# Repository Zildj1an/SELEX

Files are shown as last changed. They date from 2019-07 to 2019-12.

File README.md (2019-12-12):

# SELEX Process with Artificial Intelligence 👨‍🔧

 




## [0] Introduction 📄

This was a long project that involved:

 * [1] The robotic automatization of biotechnological protocols.
 
      All the custom hardware design can be found at OT_Robot/harware_design.
 * [2] The usage of Artifical Intelligence.
 * [3] A search engine.
 * [4] A tool to migrate WordPress websites to the iGem servers.
 * [5] And many, many custom hardware.

You can find information on installation and usage at the end [5] and our <a href = "https://2019.igem.org/Team:MADRID_UCM/Hardware">website</a>.

## [1] Biotechnological Designs 🔬

Folder OT_Robot contains biotechnological protocols for obtaining trained libraries of DNA aptamer molecules automated with the Opentrons OT-2 robot. This protocol is part of our contribution to the 2019 iGEM international biotechnology competition. For the thermocycler we built the Ninja-PCR(original from [hisashin](https://github.com/hisashin/NinjaPCR/)). More information about the entire project can be found in our <a href = "https://2019.igem.org/Team:MADRID_UCM/Landing">website</a>.

Aptamers are a cutting-edge technology that is revolutionizing biotechnology, from biosensing to synthetic biology. Aptamers are single-strand DNA molecules that hold nature’s most important information: our genetic code. But instead of using DNA for carrying information, our aptamers depend on DNA’s 3-dimensional shape. 

We genetically engineer this shape to take hold of and mesh with our target molecule. DNA’s unique role in nature gives aptamers amazing characteristics, making them robust, stable, and cheap to produce. 

The small-sized thermal cycler is controlled via motherboard Ninja-PCR Arduino-alike, as shown above, manually welded, whose code is in NinjaPCR [folder](https://github.com/Zildj1an/SELEX/tree/master/NinjaPCR). You can update a new binary since ESP8266 SystemOnChip includes the TCP/IP stack. We also recommend the usage of an external Raspberry Pi to uninterruptedly provide the robot with Wi-Fi. You can find more information about usage at [5].

 

## [2] Artificial Intelligence Algorithm: GAN network 🤖

We also did an **Artificial Intelligence algorithm** to predict the optimal DNA molecule shapes. It is a Generative adversarial network, divided in two neuronal networks: the Generative and the Discriminative. CNN nets are used. 



## [3] iGem Search Engine 🔍 

In addition, you can use our Search Engine for words in previous or this year's team's websites. This is a python search engine with GUI for searching words in each competition year and team's website.

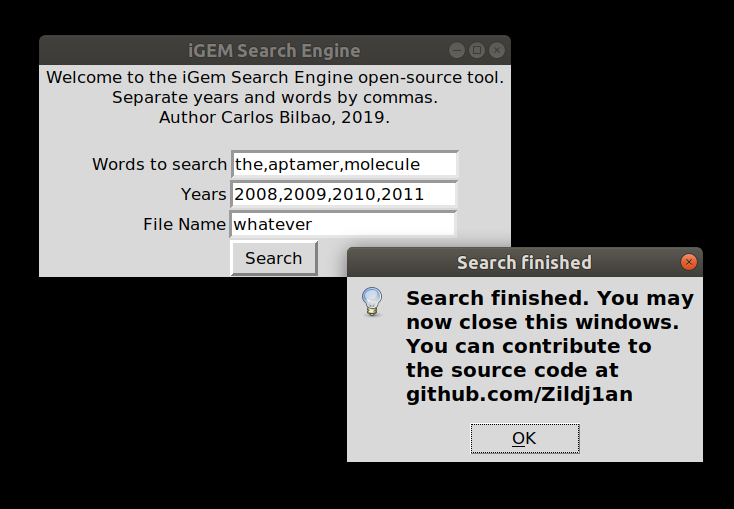
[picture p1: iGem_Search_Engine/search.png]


# [4] A tool to migrate WordPress websites to the iGem servers.

We also developed a tool to make life easier to web page developers at the iGem competition. You can use WordPress templates to develop your site and then migrate it easily with this multi-threaded script located at Tool_Migrate folder.

To run the script you can do:

```
$ bash treatment.sh [url_1] -nm - - [url_2]
```

Some additional options are available, feel free to navigate throw our code!

# [5] Hardware Design 🔋 

## Potentiostat

To assemble the potentiostat, first you should send to manufacture the PCB, in our instance we sent it to JLPCB (https://jlcpcb.com/) and buy the components listed on the Bill of Materials file. After that, you should solder those materials on the PCB. You can also request them to solder the components, if they have them.

Any team could reproduce this potentiostat sending the gerber and the NC Drill files to the manufacturer.

Regarding to the case, we designed it with a 3D modelling software, and we cut the flat faces in methacrylate with a laser cutter machine and otherwise we printed it with a 3D printer.

The PCB was made with the Altium Designer software. Altium can export PCB and schematic files as ACCEL-ASCII files. With these files you can import them to Eagle.



## Fluorimeter
To assemble the fluorimeter, you should send to manufacture the PCB, for instance we sent it to JLPCB (https://jlcpcb.com/) and buy the components listed on the Bill of Materials file. After that, you should solder those materials on the PCB. You can also request them to solder the components, if they have them.

Any team could reproduce this fluorimeter sending the gerber and the NC Drill files to the manufacturer. The PCB was made with the Altium Designer software. Altium can export PCB and schematic files as ACCEL-ASCII files. With these files you can import them to Eagle.

In relation to the case, we designed it with a 3D modelling software, and we cut the faces in methacrylate with a laser cutter machine.

## Wax Module
Wax Module
To assemble the Wax Module, you should send to manufacture the PCB, in our instance we sent it to JLPCB (https://jlcpcb.com/) and buy the components listed on the Bill of Materials file. After that, you should solder those materials on the PCB. You can also request them to solder the components, if they have them.

Any team could reproduce this module sending the gerber and the NC Drill files to the manufacturer.

The PCB was made with the Eagle software. To generate the necessary files, you can follow the JLPCB guide (https://support.jlcpcb.com/article/43-how-to-export-eagle-pcb-to-gerber-files).

In relation to the case, we designed it with a 3D modelling software, and we cut the faces with a laser cutter and the part where the resistances are located, was printed with an aluminium printer. Also, the part where the stamps are placed can be printed with a 3D printer.

## PCR, Thermal Modules
To assemble the NinjaPCR, you can make it yourself following the instructions written on their webpage or buy it (https://ninjapcr.tori.st/en/index.html).

To assemble the Thermal Module, you can send to manufacture the PCB, in our instance we sent it to JLPCB (https://jlcpcb.com/) and buy the components listed on the Bill of Materials file. After that, you should solder those materials on the PCB. You can also request them to solder the components, if they have them. The other option you could buy it from their webpage.

In relation to the case, we redesigned the NinjaPCR case with a 3D modelling software, and we cut the faces with a laser cutter in methacrylate and in wood. 

We redesigned it because we used another fan.



## Shaker Module
To assemble the Shaker Module, you should send to manufacture the PCB, in our instance we sent it to JLPCB (https://jlcpcb.com/) and buy the components listed on the Bill of Materials file. After that, you should solder those materials on the PCB. You can also request them to solder the components, if they have them.

Any team could reproduce this module sending the gerber and the NC Drill files to the manufacturer.

The PCB was made with the Eagle software. To generate the necessary files, you can follow the JLPCB guide (https://support.jlcpcb.com/article/43-how-to-export-eagle-pcb-to-gerber-files).

In relation to the case, we designed it with a 3D modelling software, and we printed the module with a 3D printer.

We also designed some PCBs from ourselves to make things easier and make them fit in the robot. We used a 3D-printer for some of our designs to store Eppendorf and Falcon tipracks. We also deisgned a PCB for a potenciostat microcontroller Teensy 3.0 and an auxiliar thermic module to cool to 4 degrees Celsius, and so on.

The 3D-designs will are available at the folder OT_Robot/hardware_design

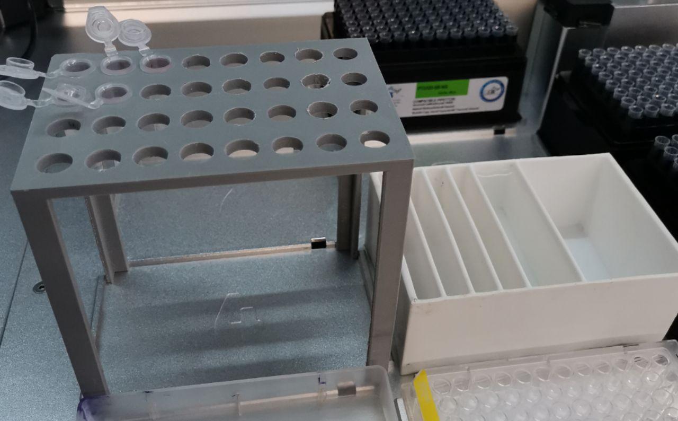
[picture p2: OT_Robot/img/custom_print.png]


## [6] Installation and Usage ❓

Our project has a lot of software involved, including:

1. A graphical Search Engine for words in websites of previous years of iGem:
   
You can run it from your terminal using:
```
$ python search.py
```
You might have some dependencies not installed, you just need to do:
```
$ sudo pip install <dependencies>	
```

2. The Aptamer Folding:

In the folder DB_Creation, execute (if you use Mac or Linux), for terminal:
```
$ python DB_Creation_Terminal.py
```
You can also speed things up with threads with bash run_several.sh, but be aware that you would need to modify the absolute path to the Rosetta software.

In the folder GAN_Network, from terminal:
```
$ python Main.py
```
Other files that could be used:

3D_structure_creation_in_pdb.py Creates only one PDB for the DDBB (testing puposes)

GAN_Network.py (Same thing as GAN_Network folder but in one file)

3. OT_Robot protocols

It contains tons of biotechnological protocols automated for the Opentrons OT2 robot in Python. The most important one is the SELEX process. To run these protocols you just need to drug and drop the protocols into the OT2 app.

You can also find in here the hardware design.

You can clone this repo or download the zip. Make sure all the dependencies are covered. First line is for installation of pip at most Linux distributions.

```
$ sudo apt install python-pip || pacman -S python-pip
$ sudo pip install opentrons subprocess time os
```
The robot uses the audio robot.mp3 and gets it from Robot Raspberry's /mnt/usbdrive/ (put it there or edit the location).
You can load the protocol in the Opentrons application, available <a href = "https://opentrons.com/ot-app">here</a>.
We also recommend the usage of an external Raspberry Pi to uninterruptedly provide the robot with Wi-Fi. Once you have stablished the Wi-Fi network at the Raspberry, you can connect the Robot too:

```
# nmcli dev wifi connect <userSSID> password <passwdSSID>
```
After the last update of the Robot -by the time this is written- the SSH connection has changed and now you need to exchange with it a public key for a more secure connection. Then when connected the robot will request the passphrase, at least the first time. Here is how you create the public key (you probably already have one):

```
$ ssh-keygen
Generating public/private rsa key pair.
Enter file in which to save the key (/home/.ssh/id_rsa):
/home/pepe/.ssh/id_rsa already exists.
Overwrite (y/n)?
Enter passphrase (empty for no passphrase):
Your identification has been saved in /home/.ssh/id_rsa.
Your public key has been saved in /home/.ssh/id_rsa.pub.
The key fingerprint is:
a9:49:2e:2a:5e:33:3e:a9:de:4e:77:11:58:b6:90:26 pepe@remote_host
The key's randomart image is:
+--[ RSA 2048]----+
|     ..o         |
|   E o= .        |
|    o. o         |
|        ..       |
|      ..S        |
|     o o.        |
|   =o.+.         |
|. =++..          |
|o=++.            |
+-----------------+
```

## Authors
* [Pablo Villalobos](https://github.com/pablo-vs)
* [Carlos Bilbao](https://github.com/Zildj1an)
* [Ana Matesanz](https://github.com/anamatesanz)
* [Irene Guardiola](https://github.com/Irene-G)
* Francisco Javier Quero

## License
This project's source code is licensed under the GNU-GPL License - see the <a href="https://github.com/Zildj1an/SELEX/blob/master/LICENSE">LICENSE.md</a> file for details. The other parts of the project have the Creative Commons license, as stated in the competition guidelines.

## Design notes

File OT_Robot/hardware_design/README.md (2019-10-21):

# Hardware Design

## Potentiostat

To assemble the potentiostat, first you should send to manufacture the PCB, in our case we sent it to JLPCB (https://jlcpcb.com/), and buy the components listed on the Bill of Materials file. After that, you should solder those materials on the PCB. You can also request them to solder the components, if they have them.
To be able to plug the electrode, we welded three pins into it.

Any team could reproduce this potentiostat sending the gerber and the NC Drill files to the manufacturer.

Regarding to the case, we designed it with a 3D modelling software, and we cut the flat faces in methacrylate with a laser cutter machine and otherwise we printed it with a 3D printer.

The PCB was made with the Altium Designer software. Altium can export PCB and schematic files as ACCEL-ASCII files. With these files you can import them to Eagle.

## Fluorimeter
To assemble the fluorimeter, you should send to manufacture the PCB, for instance we sent it to JLPCB (https://jlcpcb.com/) and buy the components listed on the Bill of Materials file. After that, you should solder those materials on the PCB. You can also request them to solder the components, if they have them.

Any team could reproduce this fluorimeter sending the gerber and the NC Drill files to the manufacturer. The PCB was made with the Altium Designer software. Altium can export PCB and schematic files as ACCEL-ASCII files. With these files you can import them to Eagle.

In relation to the case, we designed it with a 3D modelling software, and we cut the faces in methacrylate with a laser cutter machine.

## Wax Module

To assemble the Wax Module, you should send to manufacture the PCB, in our instance we sent it to JLPCB (https://jlcpcb.com/) and buy the components listed on the Bill of Materials file. After that, you should solder those materials on the PCB. You can also request them to solder the components, if they have them.

Any team could reproduce this module sending the gerber and the NC Drill files to the manufacturer.

The PCB was made with the Eagle software. To generate the necessary files, you can follow the JLPCB guide (https://support.jlcpcb.com/article/43-how-to-export-eagle-pcb-to-gerber-files).

In relation to the case, we designed it with a 3D modelling software, and we cut the faces with a laser cutter and the part where the resistances are located, was printed with an aluminium printer. Also, the part where the stamps are placed can be printed with a 3D printer.
The first design was made with PLA, however it got too hot and we melted it, thus the next design was made in aluminium, additionally it is a better conductor of heat. 

## PCR, Thermal Modules

To assemble the NinjaPCR, you can make it yourself following the instructions written on their webpage or buy it (https://ninjapcr.tori.st/en/index.html). 
To automatize the lid you just have to print the Engine_Support 3D model and buy the DS3225 25Kg servomotor.

The PCB of the Thermal Module is assembled in the same way as the potentiostat.
The other option is buying it from their webpage.

In relation to the case, we redesigned the NinjaPCR case with a 3D modelling software, and we cut the faces with a laser cutter in methacrylate and in wood. We had to redesign the case because the fan we used was too big in comparition to the one the NinjaPCR uses.
At the beginnig we bougth the ARCTIC Freezer 11 LP fan, but it did not dissipate enough heat and the peltier cell started getting hot, therefore we changed it to SilverStone SST-AR06. With this one was enough, but at some point it broke down and we finally changed it to ARCTIC F12 - 120 mm.

## Shaker Module

The PCB of the Shaker Module is assembled in the same way as the potentiostat. Like the Wax Module, most of the components were soldered by the manufacturer.

The PCB was made with the Eagle software. To generate the necessary files, you can follow the JLPCB guide (https://support.jlcpcb.com/article/43-how-to-export-eagle-pcb-to-gerber-files).

In relation to the case, we designed it with a 3D modelling software, and we printed the module with a 3D printer.

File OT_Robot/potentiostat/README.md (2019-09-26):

# Potentiostat controller

Makefile and teensy libraries cloned from https://github.com/apmorton/teensy-template
Configured for Teensy 3.2

Potentiostat library adapted from https://bitbucket.org/iorodeo/potentiostat/src/default/

Setup
-----

Install the Teensy udev rule: `sudo cp tools/49-teensy.rules /etc/udev/rules.d/`

Then unplug your Teensy and plug it back in.

Using
-----

1. Put your code in `src/main.cpp`
2. Put any libraries you need in `libraries`
3. Set the TEENSY variable in `Makefile` according to your teensy version
4. Build your code ```make```
5. Upload your code ```make upload```

Make Targets
------------

- `make` alias for `make hex`
- `make build` compiles everything and produces a .elf
- `make hex` converts the elf to an intel hex file
- `make post_compile` opens the launcher with the correct file
- `make upload` uploads the hex file to a teensy board
- `make reboot` reboots the teensy

Where everything came from
--------------------------

- The `teensy3` sub-folder is taken from [The Teensy 3 Cores](https://github.com/PaulStoffregen/cores/tree/master/teensy3)
- The `tools` sub-folder is taken from [Teensyduino](http://www.pjrc.com/teensy/td_download.html)
- The `src/main.cpp` file is moved, unmodified from `teensy3/main.cpp`
- The `Makefile` file is moved, modified from `teensy3/Makefile`
- The `49-teensy.rules` file is taken from [PJRC's udev rules](http://www.pjrc.com/teensy/49-teensy.rules)

Modifications to `Makefile` include
- Add support for arduino libraries
- Change tools directory
- Calculate target name from current directory
- Prettify rule output
- Do not upload by default, only build

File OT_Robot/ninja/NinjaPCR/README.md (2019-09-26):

# Thermocycler controller

This is the original NinjaPCR software, modified to allow OTA updates and control the automated lid.

The lid will automatically open when the system boots, close when a program starts, and open again when it is completed or stopped.

You can use the OTA updater via "http://\<address\>/update"

NOTE: we were unable to use mDNS to connect to the server, so to control the module you'll have to either use it in AP mode, get your DHCP server to assign it a fixed IP, or manually find the IP address each time using, for example, nmap.

NOTE: For the automated lid to work, a pin must be used to control the servo. Since there are no free pins in the NinjaPCB, we use the least-used one: the RX pin. The downside is that the serial port can no longer be used to communicate with the thermocycler, but maybe you can get it to still transmit debug info over TX. For the moment all uses of the Serial class have been disabled. Change ENABLE_AUTOMATIC_LID in board_conf_ninjapcr_wifi.h to enable Serial again.

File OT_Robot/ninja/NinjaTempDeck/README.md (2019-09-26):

# Thermal module controller

This is the original NinjaPCR software, modified to allow OTA updates and work without the lid thermistor and controller.

You can load any program that the NinjaPCR will accept, it will just ignore the lid temperature setting.

You can use the OTA updater via "http://\<address\>/update"

NOTE: we were unable to use mDNS to connect to the server, so to control the module you'll have to either use it in AP mode, get your DHCP server to assign it a fixed IP, or manually find the IP address each time using, for example, nmap.

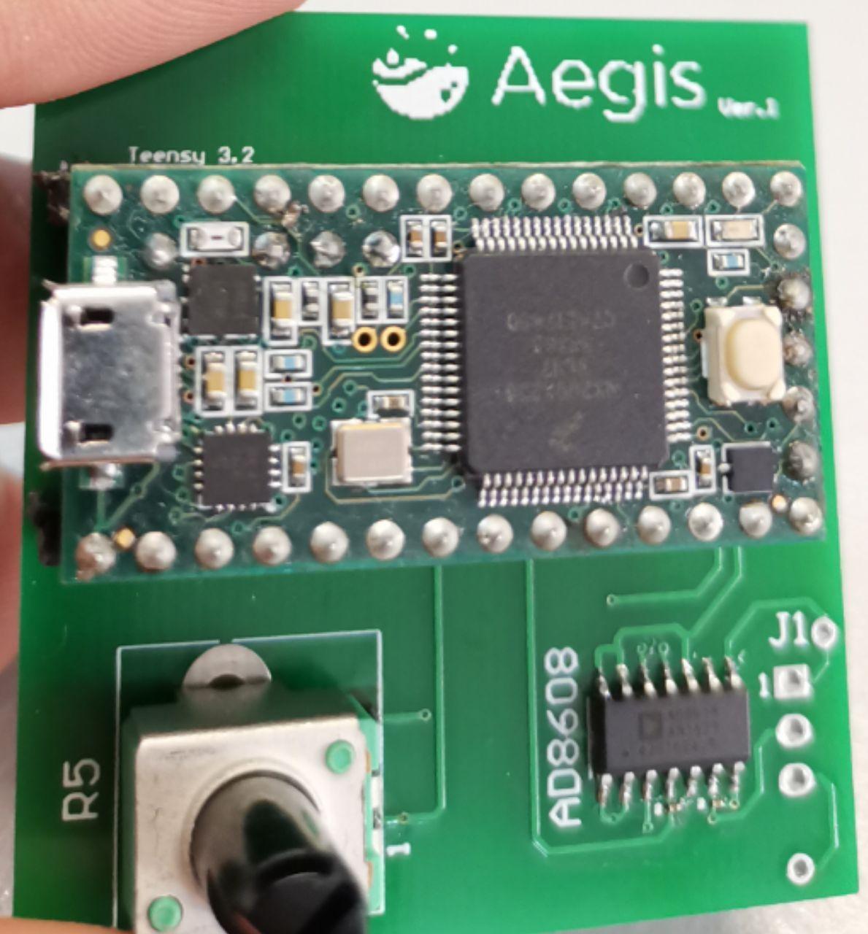
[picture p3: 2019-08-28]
OT_Robot/img/potencio.png

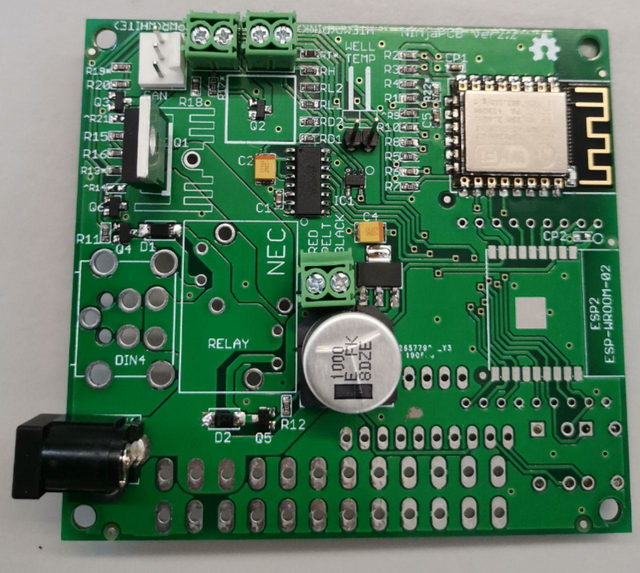
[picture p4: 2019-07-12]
OT_Robot/img/ninja.png

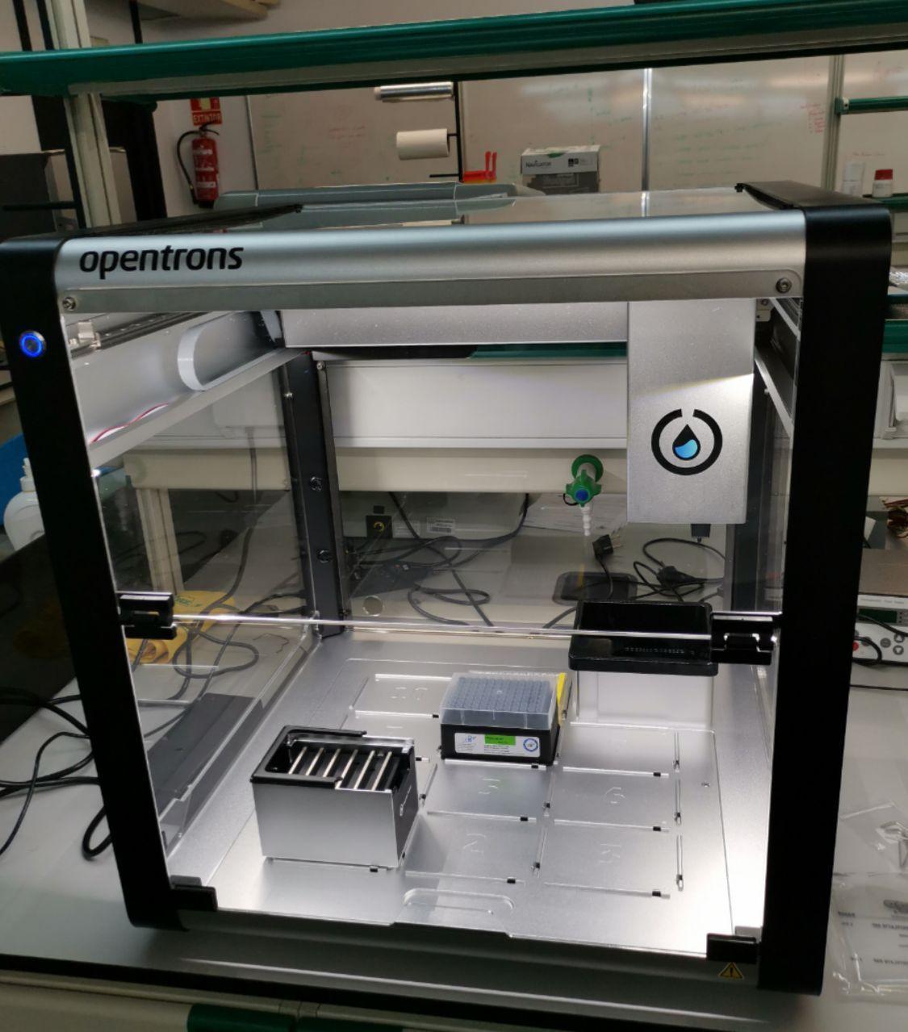
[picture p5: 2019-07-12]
OT_Robot/img/robot.jpg

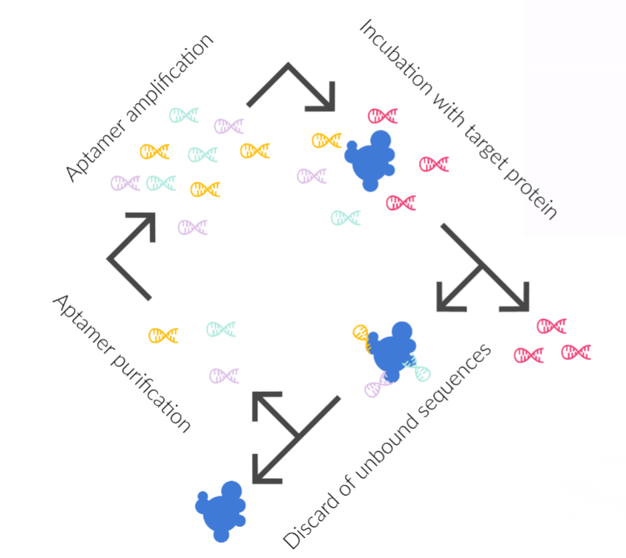
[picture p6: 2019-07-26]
OT_Robot/img/aptameros.png

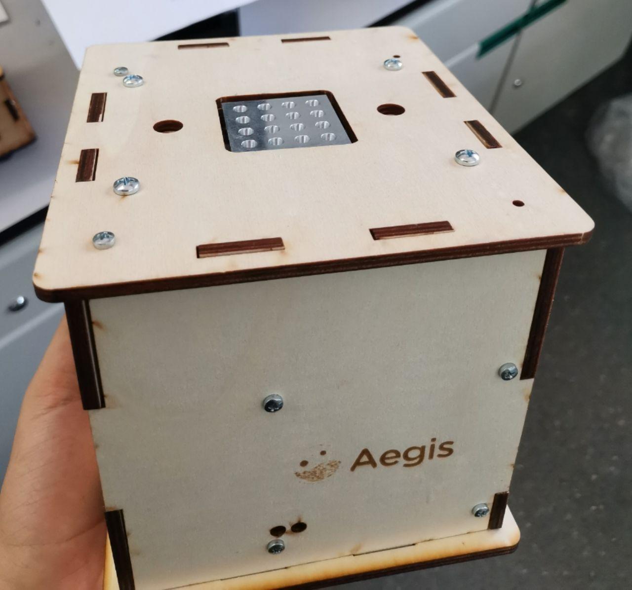
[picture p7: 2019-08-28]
OT_Robot/img/termaux.png

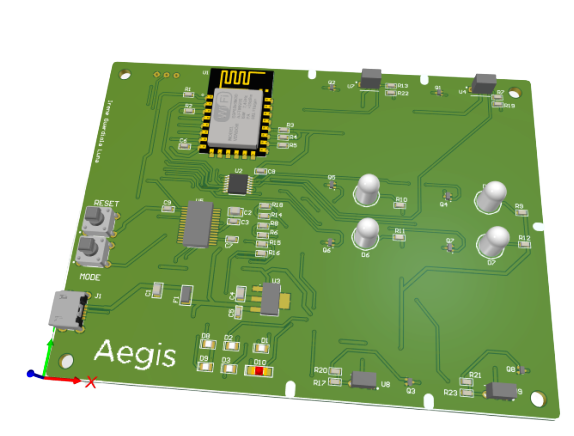
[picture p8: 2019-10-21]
OT_Robot/img/pcbb.png

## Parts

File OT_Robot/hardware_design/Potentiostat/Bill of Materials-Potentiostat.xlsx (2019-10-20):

Aegis Potentiostat BOM
Component | Description | Digi-Key Part # | Mouser Part # | Datasheet | Designator | Quantity | Price ($) | Subtotals ($)
Caps
100nF | CAP CER 0.1UF 6.3V X5R 0201 | 490-16364-1-ND |  | https://search.murata.co.jp/Ceramy/image/img/A01X/G101/ENG/GRM033R60J104JE19-01.pdf | C1, C4, C5, C6, C7 | 5 | 0.1 | 0.5
10nF | CAP CER 10000PF 10V X7R 0201 | 478-10776-1-ND |  | http://datasheets.avx.com/X7RDielectric.pdf | C2, C3 | 2 | 0.1 | 0.2
Resistors
845Ohm | RES SMD 845 OHM 0.5% 1/10W 0603 | 311-845DCT-ND |  | http://www.yageo.com/documents/recent/PYu-RT_1-to-0.01_RoHS_L_11.pdf | R1 | 1 | 0.2 | 0.2
29.4KOhm | RES SMD 29.4KOHM 0.5% 1/16W 0603 | RR08P29.4KDCT-ND |  | https://www.susumu.co.jp/common/pdf/n_catalog_partition05_en.pdf | R2 | 1 | 0.11 | 0.11
1.2KOhm | RES SMD 1.2K OHM 0.5% 1/16W 0402 | RR05P1.2KDCT-ND |  | https://www.susumu.co.jp/common/pdf/n_catalog_partition05_en.pdf | R3 | 1 | 0.1 | 0.1
16.2KOhm | RES SMD 16.2K OHM 1% 1/8W 0805 | YAG5976CT-ND |  | http://www.yageo.com/documents/recent/PYu-RT_1-to-0.01_RoHS_L_11.pdf | R4 | 1 | 0.1 | 0.1
5KOhm | Thick Film Resistors - SMD 5K ohm 1% 50V General Purpose |  | 603-RC0402FR-075KL | https://eu.mouser.com/datasheet/2/447/PYu-RC_Group_51_RoHS_L_10-1527934.pdf | R5 | 1 | 0.1 | 0.1
ICs
AD8608 | IC OPAMP GP 4 CIRCUIT 14SOIC | AD8608ARZ-ND |  | https://www.analog.com/media/en/technical-documentation/data-sheets/AD8605_8606_8608.pdf | AD8608 | 1 | 4.82 | 4.82
Teensy3.2 | Teensy USB Board, Version 3.2 |  |  |  | Teensy 3.2 | 1 | 19.8 | 19.8
 |  |  |  |  |  |  | TOTAL: | 25.93 | $

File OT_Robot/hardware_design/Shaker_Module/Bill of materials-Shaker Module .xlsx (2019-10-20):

Aegis Shaker Module BOM
Component | Description | Digi-Key Part # | Datasheet | Designator | Quantity | Price ($) | Subtotals ($)
Caps
10uF |  |  | https://www.alldatasheet.com/datasheet-pdf/pdf/120370/ETC1/CC1206.html | C1 | 1 | 0.08 | 0.08
Resistors
10kOhm | 10KOHM-0603-1/10W-1% |  |  | R1, R2, R3, R4 | 4 | 0.0016 | 0.0064
ICs
LM1117MP-3.3 | 800mA Low-Dropout Linear Regulator | LM1117MP-3.3/NOPBCT-ND | http://www.ti.com/lit/ds/symlink/lm1117.pdf | IC1 | 1 | 1.14 | 1.14
ESP12E | Microcontroller + Wifi |  |  | SJR1 | 1 | 1.16 | 1.16
A4988_STEP |  |  | https://www.alldatasheet.com/datasheet-pdf/pdf/338780/ALLEGRO/A4988.html | US1 | 1 | 1.026 | 1.026
Other Supplies
Switch | OMRON SWITCH |  |  | S1, S2 | 2 | 0.25 | 0.5
Stepper Motor
 |  |  |  |  |  | TOTAL: | 3.9124 | $

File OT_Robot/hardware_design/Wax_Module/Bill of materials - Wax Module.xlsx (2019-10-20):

Aegis Wax Module BOM
Component | Description | Digi-Key Part # | Designator | Datasheet URL | Quantity | Price ($) | Subtotals ($)
Caps
10UF | CAPACITOR, European symbol |  | C1 | pdf/pdf/120370/ETC1/CC1206.html | 1 | 0.08 | 0.08
Resistors
10KOhm | 10KOHM-0603-1/10W-1% |  | R1, R2, R3, R4,R5 |  | 5 | 0.0016 | 0.008
ICs
LM1117MP-3.3 | 800mA Low-Dropout Linear Regulator | LM1117MP-3.3/NOPBCT-ND | IC1 | http://www.ti.com/lit/ds/symlink/lm1117.pdf | 1 | 1.14 | 1.14
MOSFET-NCH-2N7002PW | N-channel MOSFETs |  | Q2 | https://docs-emea.rs-online.com/webdocs/1206/0900766b812062e7.pdf | 1 | 0.27 | 0.27
ESP12E | Microcontroller + Wifi |  | SJR1 |  | 1 | 1.16 | 1.16
Other Supplies
Switch | OMRON SWITCH |  | S1, S2 | https://www.alldatasheet.com/datasheet-pdf/pdf/206803/OMRON/B3F-1000.html | 2 | 0.25 | 0.5
 |  |  |  |  |  | TOTAL: | 3.158 | $

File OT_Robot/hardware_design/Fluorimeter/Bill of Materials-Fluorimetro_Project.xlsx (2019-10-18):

Aegis Potentiostat BOM
Component | Description | Mouser Part # | RS Part # | Designator | Datasheet URL | Quantity | Price ($) | Subtotals ($)
Caps
100nF | Multilayer Ceramic Capacitors MLCC - SMD/SMT 0603 MLCC X7R 0.1 uF+/- 5% 16 V T&R GP | 791-0603B104J160CT |  | C3, C5, C6, C7, C8, C9 | https://eu.mouser.com/datasheet/2/210/WTC_MLCC_General_Purpose-1534899.pdf | 6 | 0.12 | 0.72
10nF | Multilayer Ceramic Capacitors MLCC - SMD/SMT 0805 MLCC NPO 0.01 uF+/- 1% 50 V T&R GP | 791-0805N103F500CT |  | C1 | https://eu.mouser.com/datasheet/2/210/WTC_MLCC_General_Purpose-1534899.pdf | 1 | 0.347 | 0.347
4,7nF | Multilayer Ceramic Capacitors MLCC - SMD/SMT 10V 4.7uF 5% X7R AUTO | 80-C0805C475J8RAUTO |  | C2, C4 | https://eu.mouser.com/datasheet/2/212/KEM_C1023_X7R_AUTO_SMD-1093309.pdf | 2 | 0.579 | 1.158
Resistors
66,5 Ohm | Thin Film Resistors - SMD 1/16W 66.5ohm 0.5% 50ppm | 754-RR0816Q-66R5D80R |  | R6 | https://eu.mouser.com/datasheet/2/392/susumu_RR_Data_Sheet-1206438.pdf | 1 | 0.1 | 0.1
60,4 Ohm | Thin Film Resistors - SMD 1/16W 60.4ohm 0.5% 50ppm | 754-RR0816Q-60R4D76R |  | R9, R8 | https://eu.mouser.com/datasheet/2/392/susumu_RR_Data_Sheet-1206438.pdf | 2 | 0.1 | 0.2
16 Ohm | Thin Film Resistors - SMD 1/16W 16ohm 0.5% 50ppm | 754-RR0816Q-160D |  | R10, R11, R12 | https://eu.mouser.com/datasheet/2/392/susumu_RR_Data_Sheet-1206438.pdf | 3 | 0.1 | 0.3
154 Ohm | Thick Film Resistors - SMD 154ohm 1% 1/10W | 652-CR0603FX-1540ELF |  | R15, R16 | https://eu.mouser.com/datasheet/2/54/chpreztr-777398.pdf | 2 | 0.1 | 0.2
10KOhm | Thick Film Resistors - SMD 0603 10Kohms 1% AEC-Q200 | 667-ERJ-3EKF1002V |  | R1, R2, R3, R4, R5, R7, R13, R17, R23, | https://eu.mouser.com/datasheet/2/315/AOA0000C304-1149620.pdf | 9 | 0.1 | 0.9
8,66KOhm | Thin Film Resistors - SMD 1/16W 8.66Kohm 0.5% 25ppm | 754-RR0816P-8661D91H |  | R19, R20, R21, R22, | https://eu.mouser.com/datasheet/2/392/susumu_RR_Data_Sheet-1206438.pdf | 4 | 0.1 | 0.4
ICs
SN74HC4066 | Analogue Switch ICs Quad Bilateral | 595-SN74HC4066PWR |  | U2 | http://www.ti.com/lit/ds/symlink/sn74hc4066.pdf | 1 | 0.49 | 0.49
ZLDO1117G33 | LDO Voltage Regulators LDO Regulator IC 3.3V/1A | 522-ZLDO1117G33TA |  | U3 | https://eu.mouser.com/datasheet/2/115/ZLDO1117-607727.pdf | 1 | 0.47 | 0.47
2SC5646A | Bipolar Transistors - BJT BIP NPN 30MA 4V FT=10G | 863-2SC5646A-TL-H |  | Q1, Q2, Q3, Q8 | https://eu.mouser.com/datasheet/2/308/ENA1120-D-118663.pdf | 4 | 0.38 | 1.52
FT232R | USB Interface IC FT232R Single Ch Full Speed | 895-FT232RL-TUBE |  | U5 | https://eu.mouser.com/datasheet/2/163/DS_FT232R-11534.pdf | 1 | 4.5 | 4.5
DMG1012T | MOSFET MOSFET N-CHANNEL SOT-523 | 621-DMG1012T-7 |  | Q4, Q5, Q6, Q7 | https://eu.mouser.com/datasheet/2/115/ds31783-44973.pdf | 4 | 0.29 | 1.16
ESP12E | Microcontroller + Wifi |  |  | U1 | https://wiki.ai-thinker.com/_media/esp8266/a014ps01.pdf | 1 | 1.16 | 1.16
Photodetector | Light To Frequency & Light To Voltage Light to Voltage Precision |  | 642-4430 | U4, U7, U8, U9 | https://eu.mouser.com/datasheet/2/588/TSL257_DS000140_2-00-932622.pdf | 4 | 2.45 | 9.8
Other Supplies
LED | Standard LEDs - Through Hole Ultraviolet (UV) 405nm 160mcd 30deg | 593-VAOL5GUV0T4 |  | D7 | https://eu.mouser.com/datasheet/2/423/VAOL-5GUV0T4-1064974.pdf | 1 | 0.979 | 0.979
LED | Standard LEDs - Through Hole Blue/ Water Clear 465-472nm2500mcd | 859-LTL2R3TBV3KS |  | D6 | https://eu.mouser.com/datasheet/2/239/Lite-On_LTL2R3TBV3KS-032A-1175179.pdf | 1 | 0.27 | 0.27
LED | Standard LEDs - Through Hole Green/ Water Clear 525-532nm7800mcd | 859-LTL2R3TGY3KS |  | D5 | https://eu.mouser.com/datasheet/2/239/Lite-On_LTL2R3TGY3KS-032A-1175244.pdf | 1 | 0.27 | 0.27
LED | Standard LEDs - Through Hole Amber Diffused | 859-LTL-4273 |  | D4 | http://optoelectronics.liteon.com/upload/download/DS-20-92-0267/4273.pdf | 1 | 0.12 | 0.12
Micro USB | USB Connectors WR-COM USB Micro SMT Type B Horiztl | 710-629105150521 |  | J1 | https://eu.mouser.com/datasheet/2/445/629105150521-469306.pdf | 1 | 2.1 | 2.1
Switch | Tactile Switches PTS645SH43-2 LFS | 611-PTS645SH432 |  | SW1, SW2 | https://eu.mouser.com/datasheet/2/60/pts645-965362.pdf | 2 | 0.14 | 0.28
Fuse | Resettable Fuses - PPTC PTC 8V 1206 0.75A POLYFUSE SMD THIN | 576-1206L075THYR |  | F1 | https://eu.mouser.com/datasheet/2/240/Littelfuse_PTC_1206L_Datasheet.pdf-477012.pdf | 1 | 0.44 | 0.44
LED | Standard LEDs - SMD Yellow Clear 587nm | 859-LTST-C171KSKT |  | D1 | https://eu.mouser.com/datasheet/2/239/Lite-On-LTST-C171KSKT-1175256.pdf | 1 | 0.3 | 0.3
LED | Standard LEDs - SMD Green Clear 569nm | 859-LTST-C171GKT |  | D2 | https://eu.mouser.com/datasheet/2/239/Lite-On-LTST-C171GKT-1175279.pdf | 1 | 0.26 | 0.26
LED | Standard LEDs - SMD 2.0X1.2MM BLUE SMD LED | 604-APT2012VBC/D |  | D3 | https://eu.mouser.com/datasheet/2/216/APT2012VBC-D-246130.pdf | 1 | 0.46 | 0.46
LED | Standard LEDs - SMD Red Clear 55MCD | 859-LTST-C171KRKT |  | D8, D9 | https://eu.mouser.com/datasheet/2/239/Lite-On-LTST-C171KRKT-1175280.pdf | 2 | 0.28 | 0.56
LED | Standard LEDs - SMD White 260MCD | 859-LTW-150TK |  | D10 | https://eu.mouser.com/datasheet/2/239/Lite-On-LTW-150TK-1175402.pdf | 1 | 0.46 | 0.46
Optical filter | Narrowband filter 570 nm, _25x 2 mm |  |  |  | https://item.taobao.com/item.htm?id=8615466201 | 1 | 2.27 | 2.27
Optical filter | Narrowband filter 532 nm, _22x 1,6 mm |  |  |  | https://item.taobao.com/item.htm?id=43871396239 | 1 | 22.61 | 22.61
 |  |  |  |  |  |  | TOTAL: | 54.804 | $

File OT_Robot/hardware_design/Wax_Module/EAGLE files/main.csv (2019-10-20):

Part | Value | Device | Package | Description | MF | MPN | OC_FARNELL | OC_NEWARK | PROD_ID | SPICEMODEL | SPICEPREFIX | VALUE
C1 | 10uF | CC1206 | C1206 | CAPACITOR, European symbol |  |  |  |  |  | NONE | C
FT232 |  | MA06-1 | MA06-1 | PIN HEADER |  |  | unknown | unknown
IC1 | LM1117MP-3.3 | LM1117MP-3.3 | SOT223 | 800mA Low-Dropout Linear Regulator | Texas Instruments | LM1117MP-3.3 | 9778195 | 28X3416
Q2 | 310mA/60V/1.6Ω | MOSFET-NCH-2N7002PW | SOT323 | N-channel MOSFETs |  |  |  |  | TRANS-11151 |  |  | 310mA/60V/1.6Ω
R1 | 10k | 10KOHM-0603-1/10W-1% | 0603 | 10kΩ resistor |  |  |  |  | RES-00824 |  |  | 10k
R2 | 10k | 10KOHM-0603-1/10W-1% | 0603 | 10kΩ resistor |  |  |  |  | RES-00824 |  |  | 10k
R3 | 10k | 10KOHM-0603-1/10W-1% | 0603 | 10kΩ resistor |  |  |  |  | RES-00824 |  |  | 10k
R4 | 10k | 10KOHM-0603-1/10W-1% | 0603 | 10kΩ resistor |  |  |  |  | RES-00824 |  |  | 10k
R5 | 10k | RR1206 | R1206 | RESISTOR, European symbol |  |  |  |  |  | NONE | R
S1 |  | 10-XX | B3F-10XX | OMRON SWITCH |  | B3F-1000 | 176432 | 36M3542
S2 |  | 10-XX | B3F-10XX | OMRON SWITCH |  | B3F-1000 | 176432 | 36M3542
SENSOR | 332-02 | 332-02 | 332-02 | 2 Pin - 2mm Dual Row
SJR1 |  | ESP8266-12EESP12E | ESP8266-ESP12E | ESP8266-12E Library for Eagle CAD
X1 |  | AK500/2 | AK500/2 | CONNECTOR |  |  | unknown | unknown
X2 |  | AK500/2 | AK500/2 | CONNECTOR |  |  | unknown | unknown

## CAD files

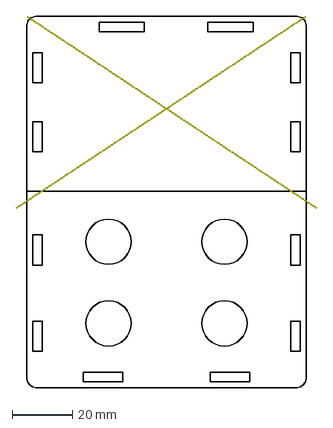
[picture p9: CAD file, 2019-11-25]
OT_Robot/hardware_design/Fluorimeter/Case/Top.dxf
99.3 x 122.8 mm

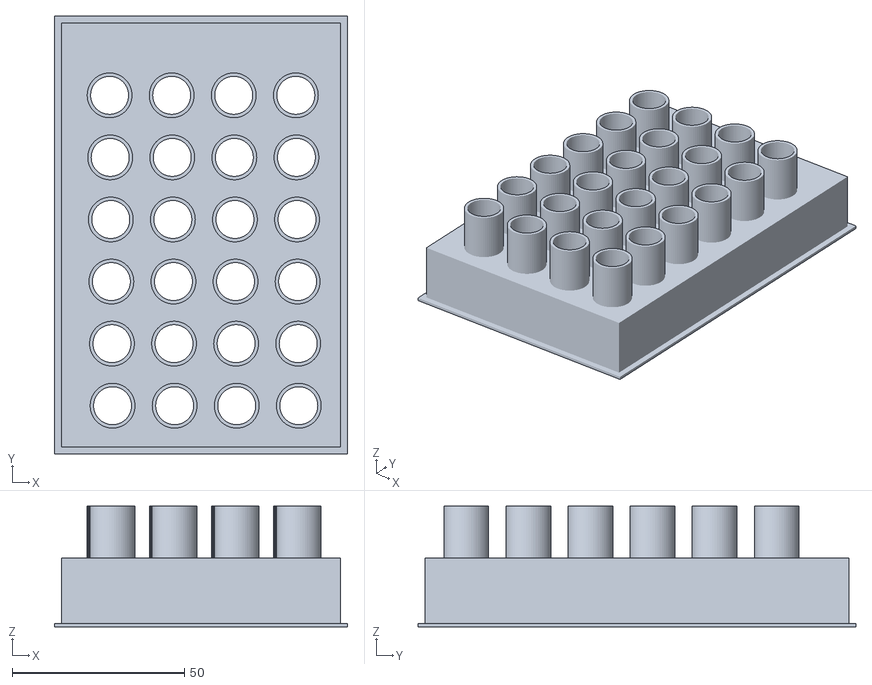
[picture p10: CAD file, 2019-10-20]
OT_Robot/hardware_design/Magnetic_Rack.stl
85.0 x 127.0 x 35.0

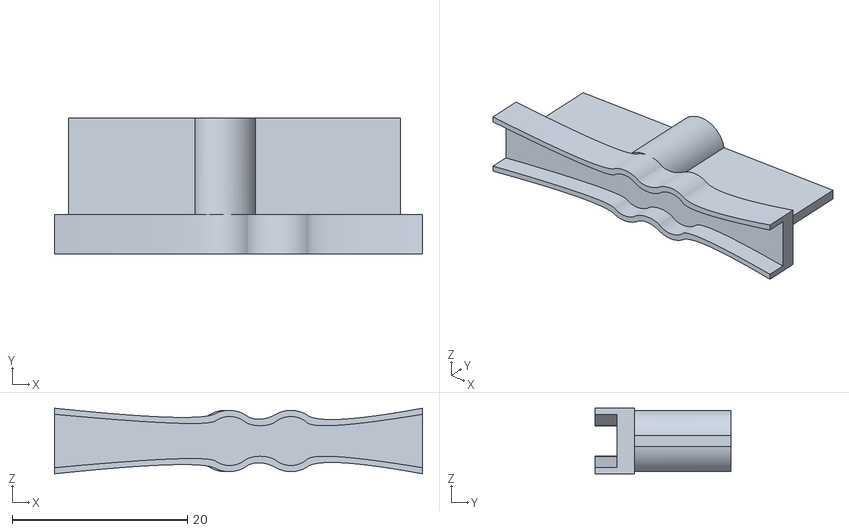
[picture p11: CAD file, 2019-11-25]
OT_Robot/hardware_design/Microfluidics/Membrane_Test_Stamp_1.stl
42.0 x 15.5 x 7.50

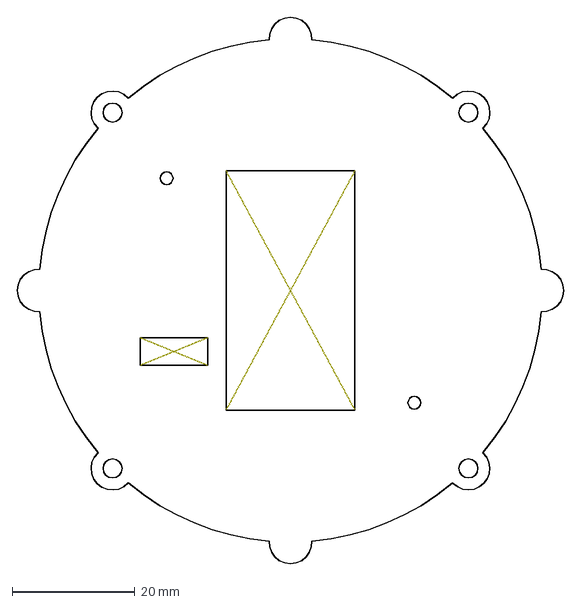
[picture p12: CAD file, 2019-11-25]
OT_Robot/hardware_design/Potentiostat/Case/Top.dxf
89.3 x 89.3 mm

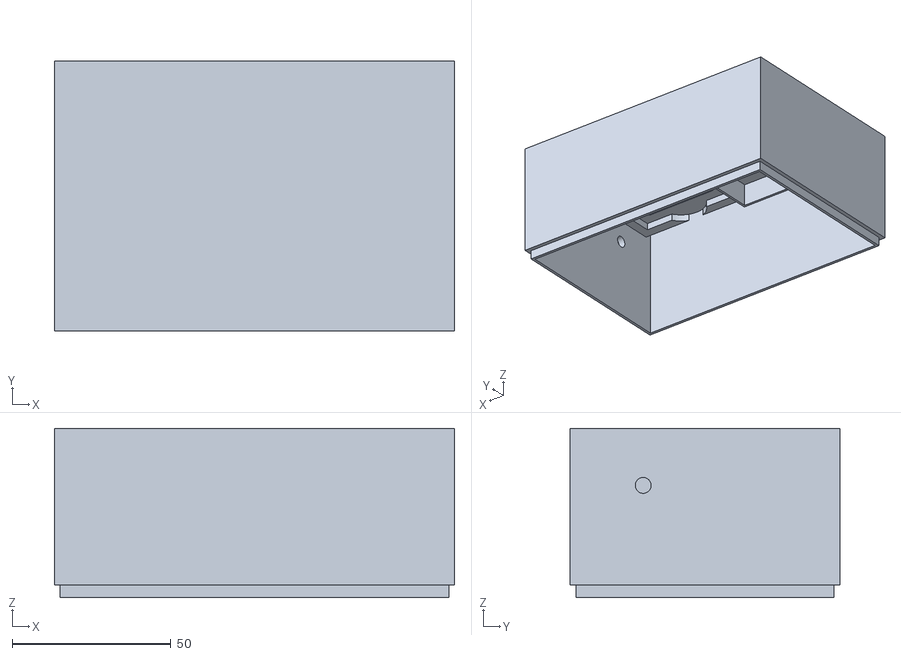
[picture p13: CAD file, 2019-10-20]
OT_Robot/hardware_design/Shaker_Module/Case/body.stl
126.0 x 85.0 x 53.3

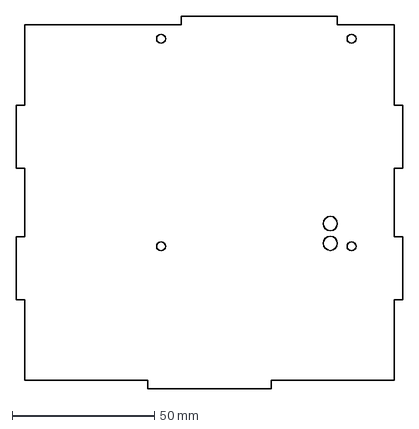
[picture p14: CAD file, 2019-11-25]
OT_Robot/hardware_design/thermal_module/PCBWood.dxf
136.0 x 131.2 mm

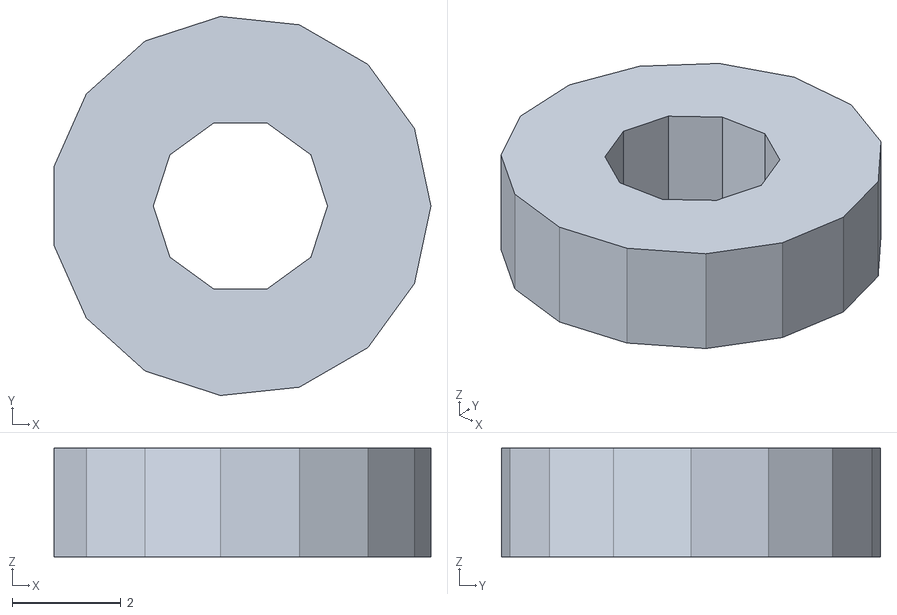
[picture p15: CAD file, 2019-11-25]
OT_Robot/hardware_design/Fluorimeter/Case/Spacer2mm.stl
6.92 x 6.96 x 2.00

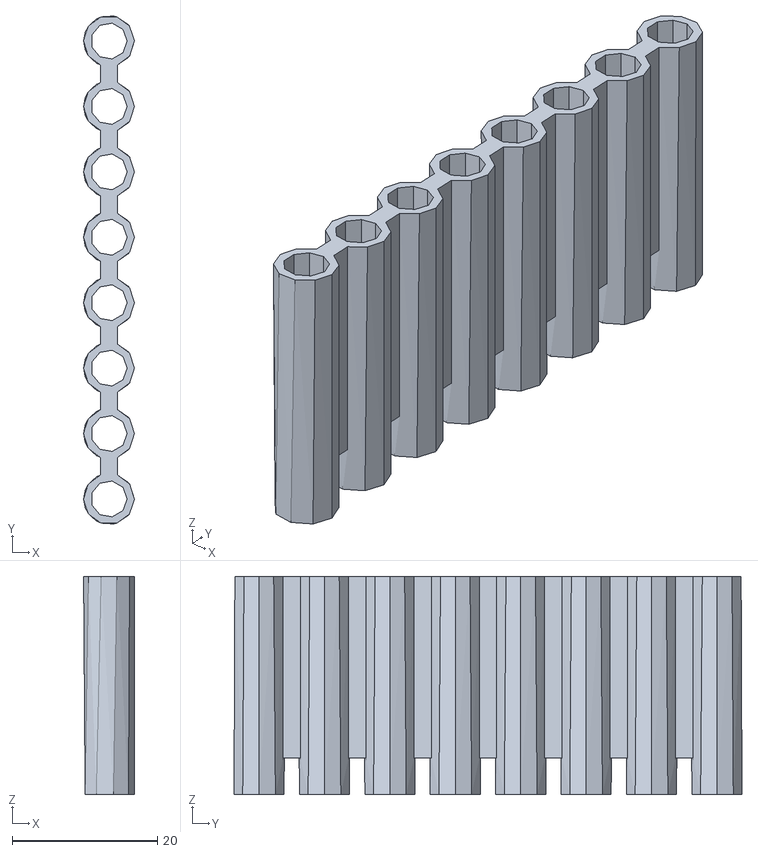
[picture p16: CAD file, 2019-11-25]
OT_Robot/hardware_design/Microfluidics/Dot Blot2.stl
7.00 x 69.9 x 30.0

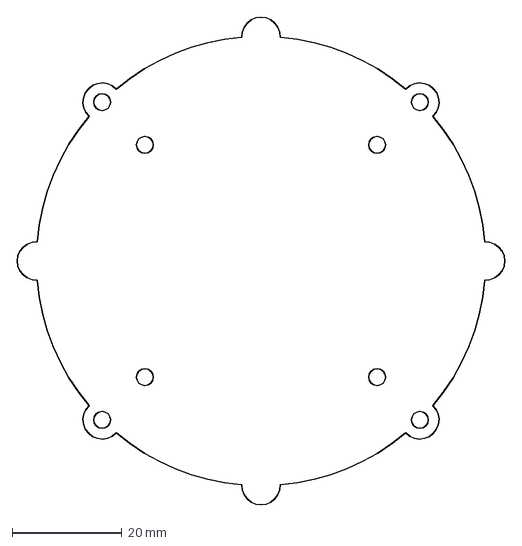
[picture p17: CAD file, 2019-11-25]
OT_Robot/hardware_design/Potentiostat/Case/Bottom.dxf
89.3 x 89.3 mm

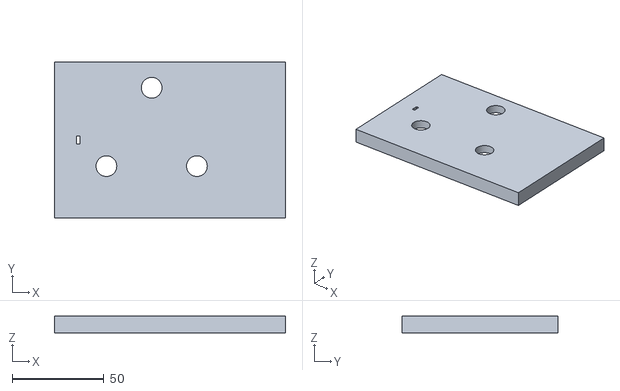
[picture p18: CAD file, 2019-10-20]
OT_Robot/hardware_design/Shaker_Module/Case/Bottom.stl
126.0 x 85.0 x 9.00

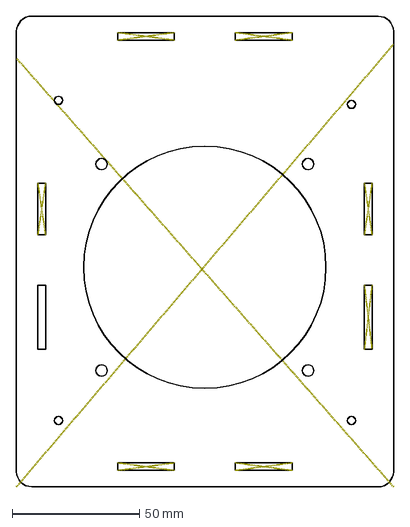
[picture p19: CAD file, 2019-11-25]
OT_Robot/hardware_design/thermal_module/Body-Bottom.dxf
147.9 x 184.6 mm

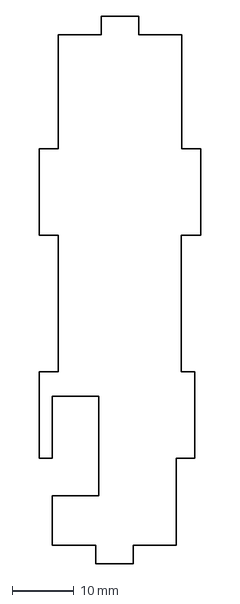
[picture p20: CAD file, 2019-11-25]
OT_Robot/hardware_design/Fluorimeter/Case/Front.dxf
26.0 x 88.3 mm

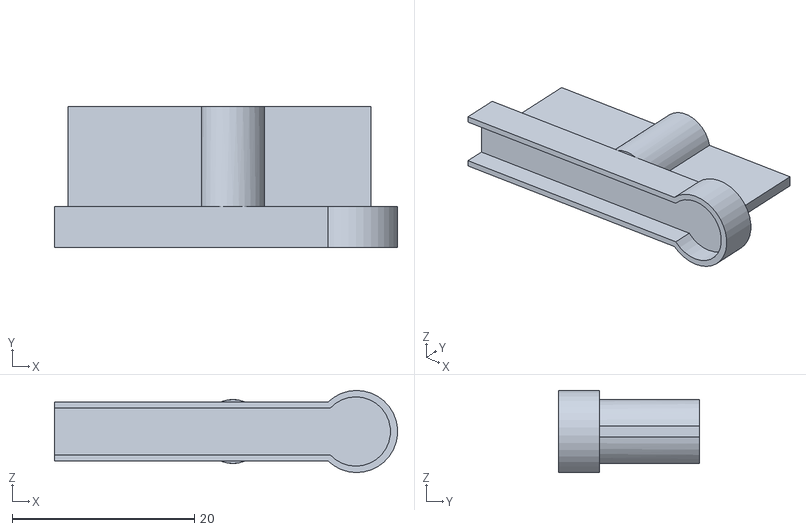
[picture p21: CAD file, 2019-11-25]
OT_Robot/hardware_design/Microfluidics/Membrane_Test_Stamp_2.stl
37.6 x 15.5 x 9.00

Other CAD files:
OT_Robot/hardware_design/NinjaPCR/body-right.dwg
OT_Robot/hardware_design/Wax_Module/Case/top.dwg
OT_Robot/hardware_design/NinjaPCR/w2004_body-left.dwg
OT_Robot/hardware_design/Wax_Module/Case/long side.dwg
OT_Robot/hardware_design/NinjaPCR/heater-lift.dwg
OT_Robot/hardware_design/Fluorimeter/Case/All.dwg
OT_Robot/hardware_design/Fluorimeter/Case/Back.dxf
OT_Robot/hardware_design/Fluorimeter/Case/Board.dxf
OT_Robot/hardware_design/Fluorimeter/Case/LSide.dxf
OT_Robot/hardware_design/Fluorimeter/Case/RSide.dxf
OT_Robot/hardware_design/Fluorimeter/Case/Walls.dxf
OT_Robot/hardware_design/Fluorimeter/Case/filter_holder1.stl
OT_Robot/hardware_design/Fluorimeter/Case/filter_holder2.stl
OT_Robot/hardware_design/Fluorimeter/Case/legs.stl
OT_Robot/hardware_design/Microfluidics/Dot Blot.stl
OT_Robot/hardware_design/Microfluidics/Membrane_Test_Stamp_3.stl
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

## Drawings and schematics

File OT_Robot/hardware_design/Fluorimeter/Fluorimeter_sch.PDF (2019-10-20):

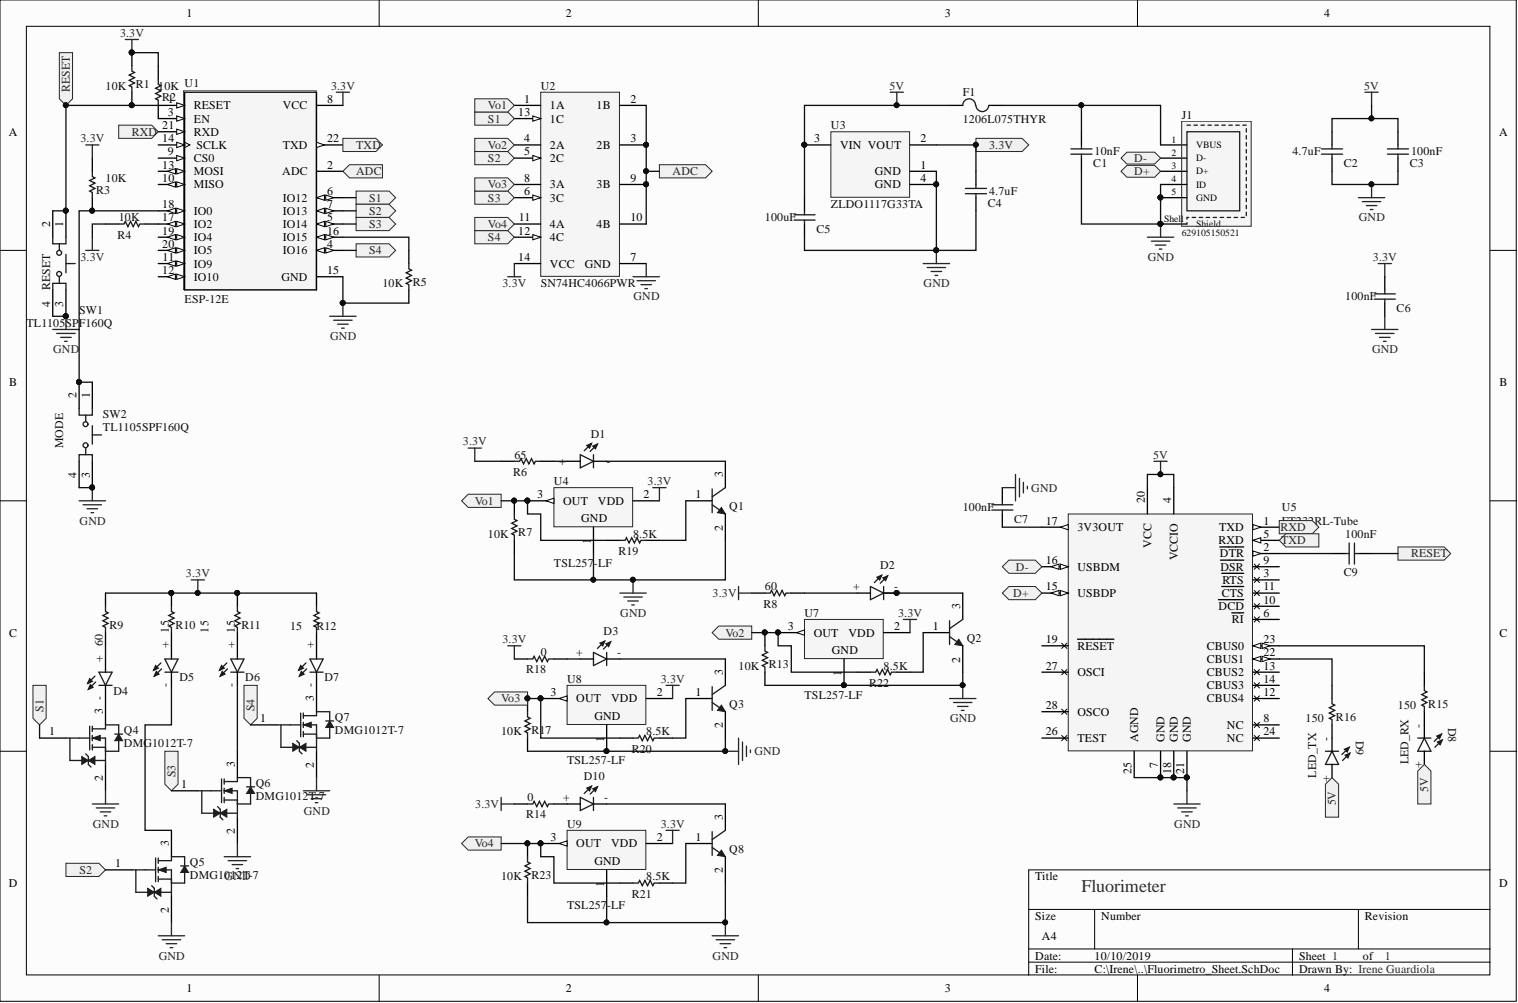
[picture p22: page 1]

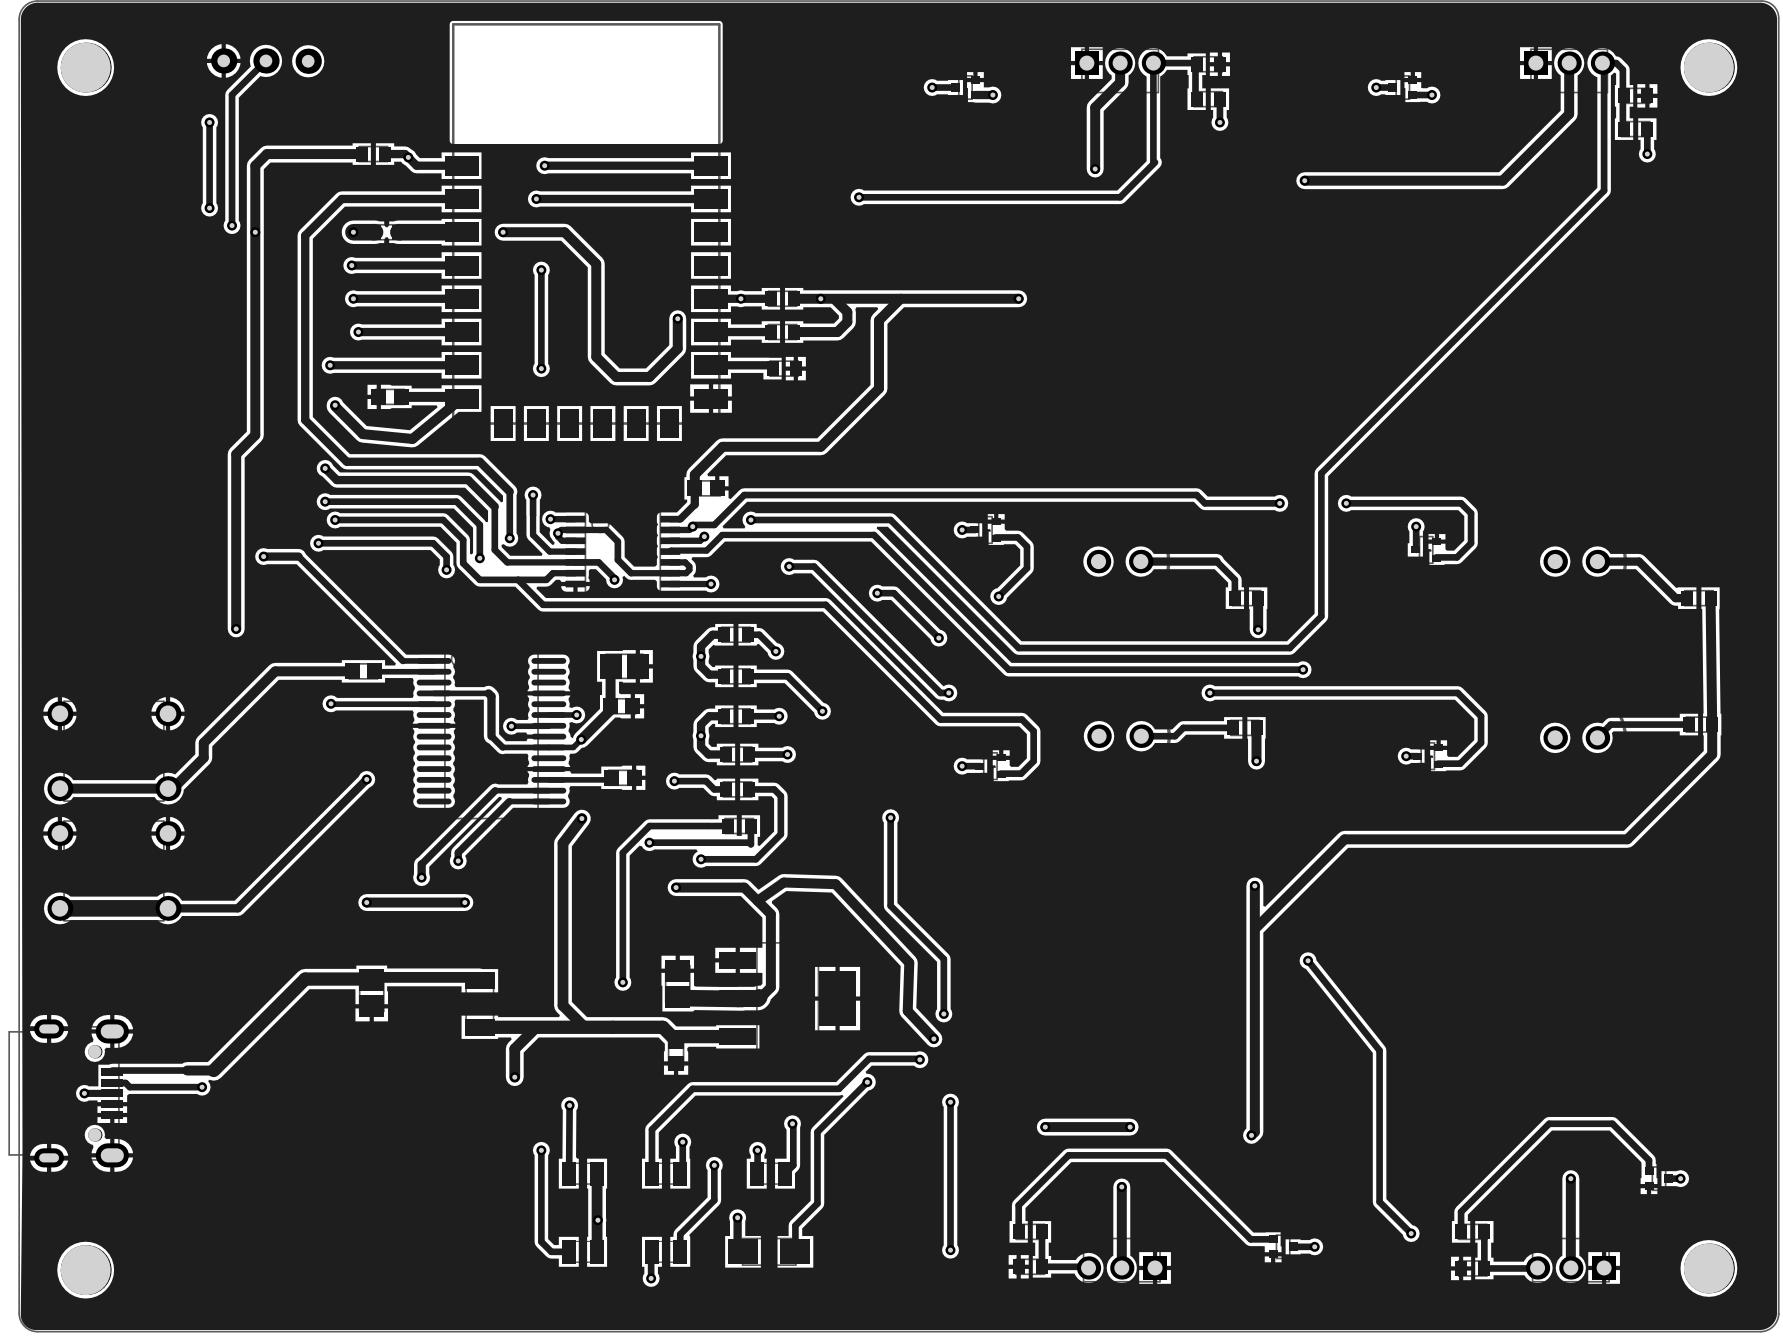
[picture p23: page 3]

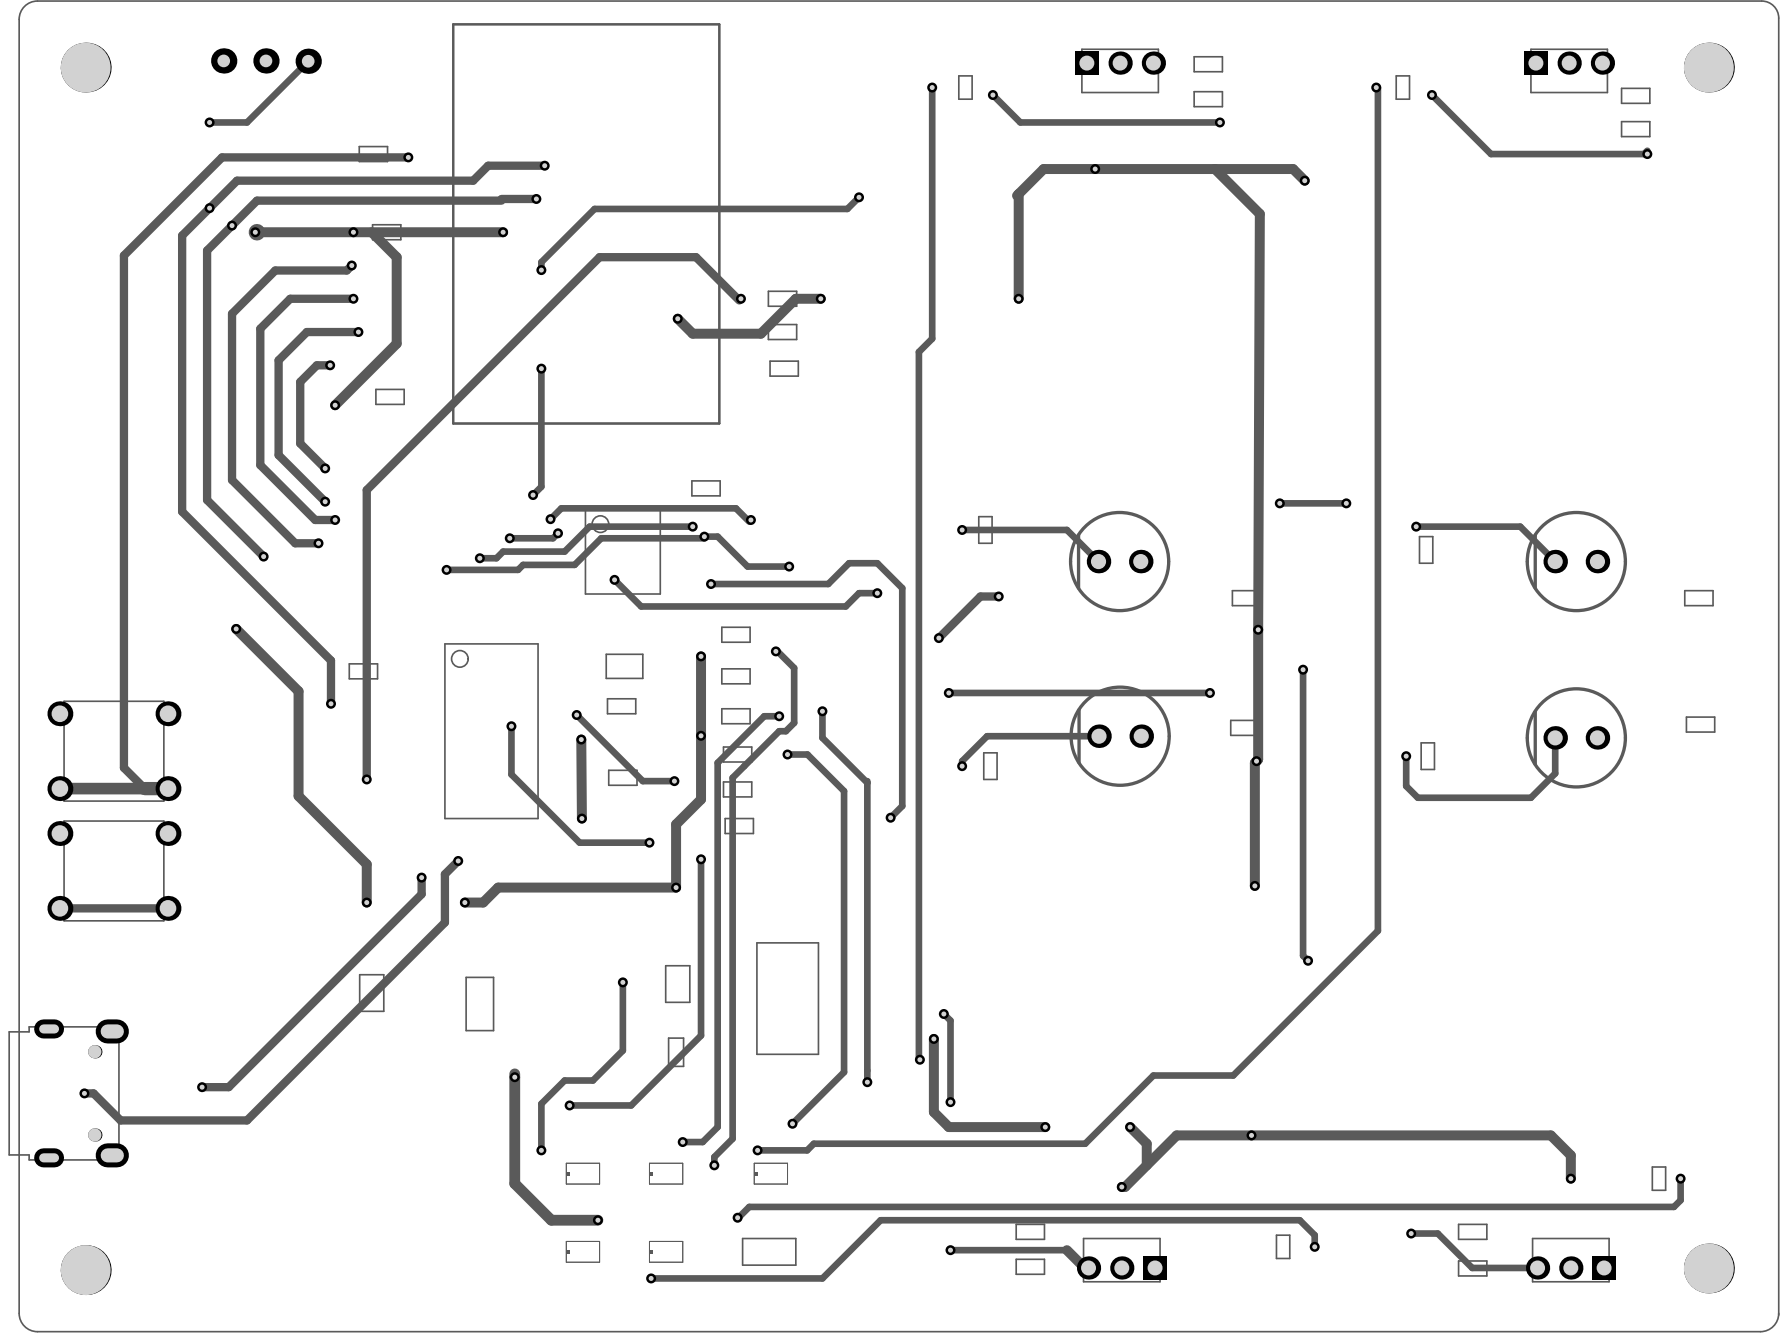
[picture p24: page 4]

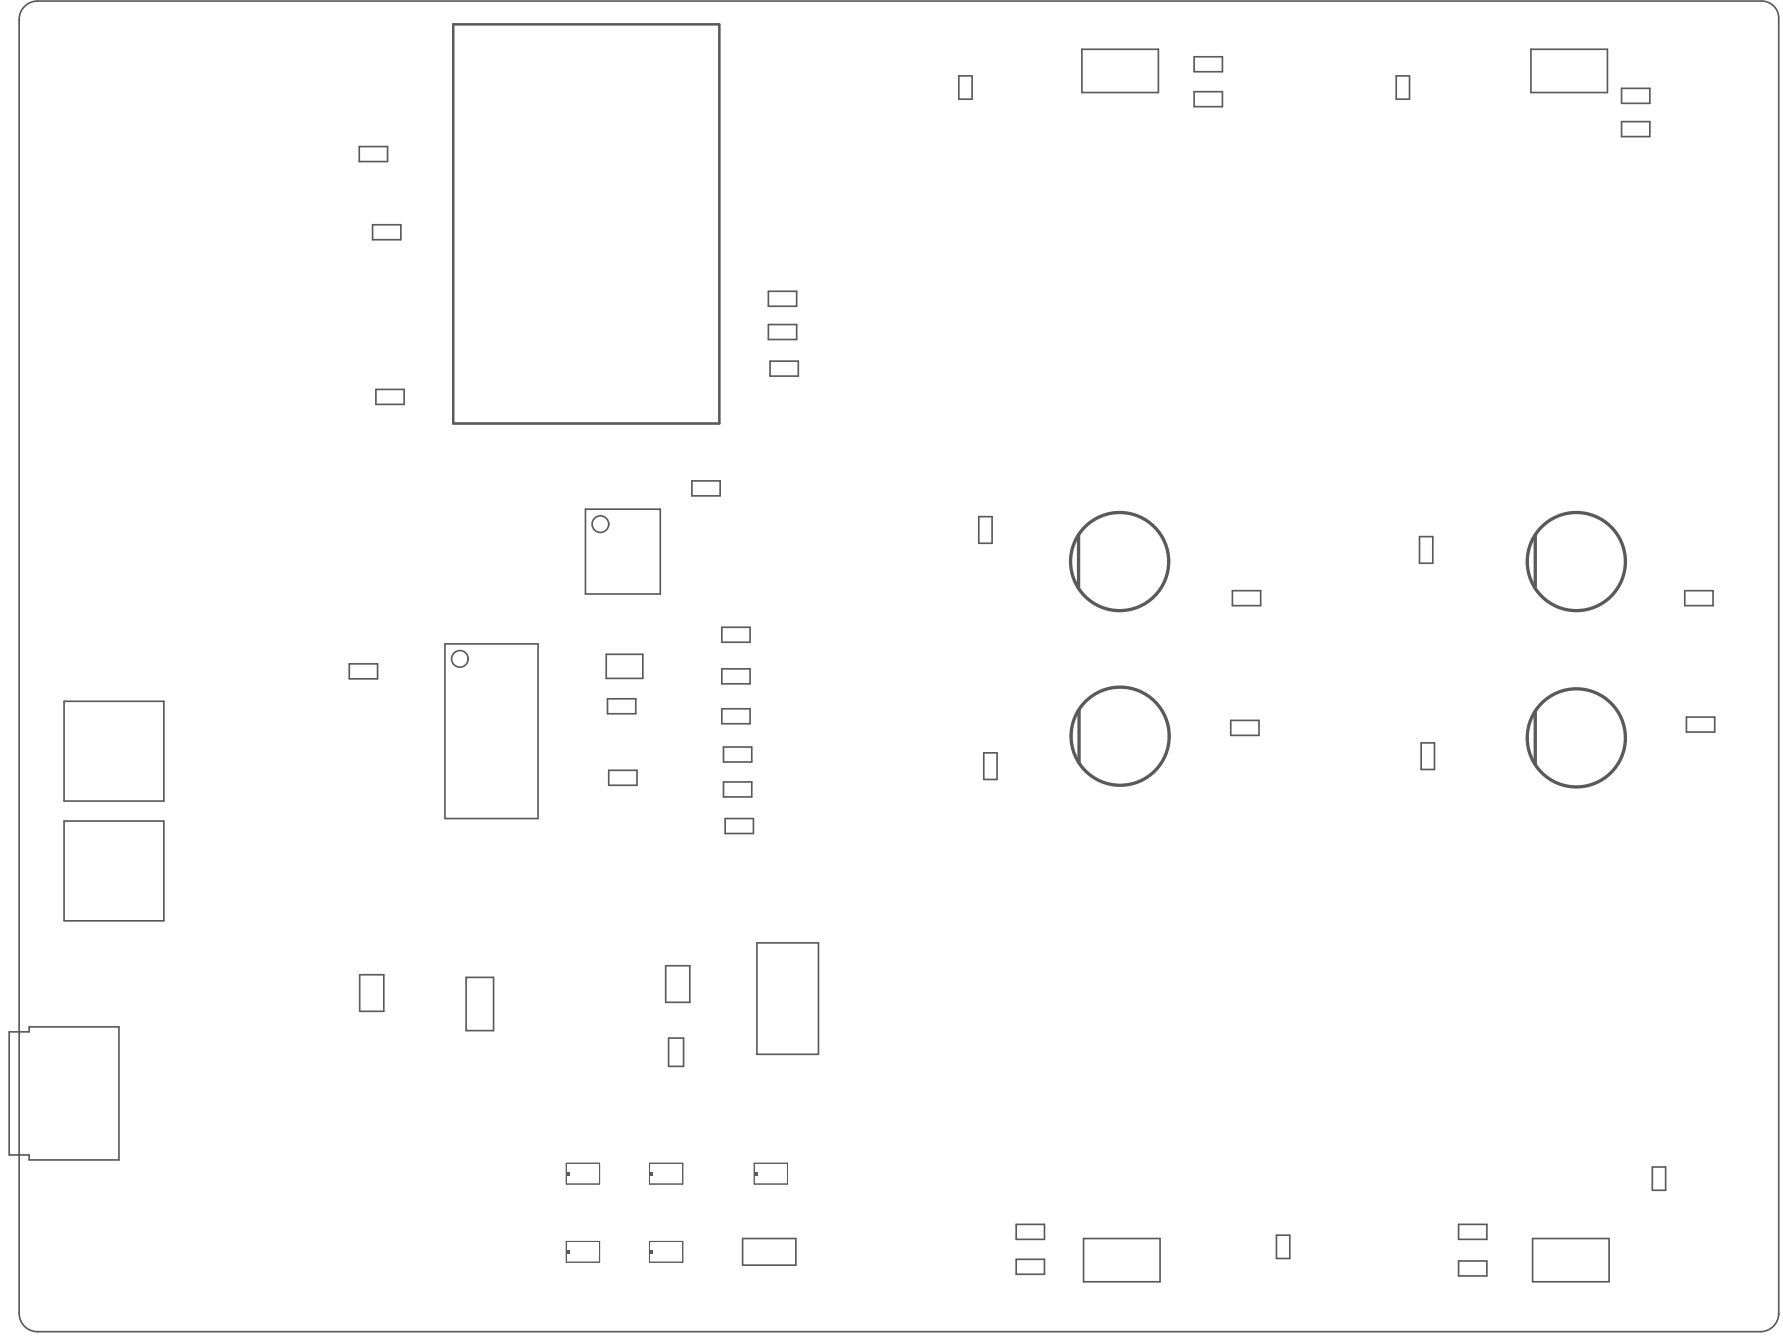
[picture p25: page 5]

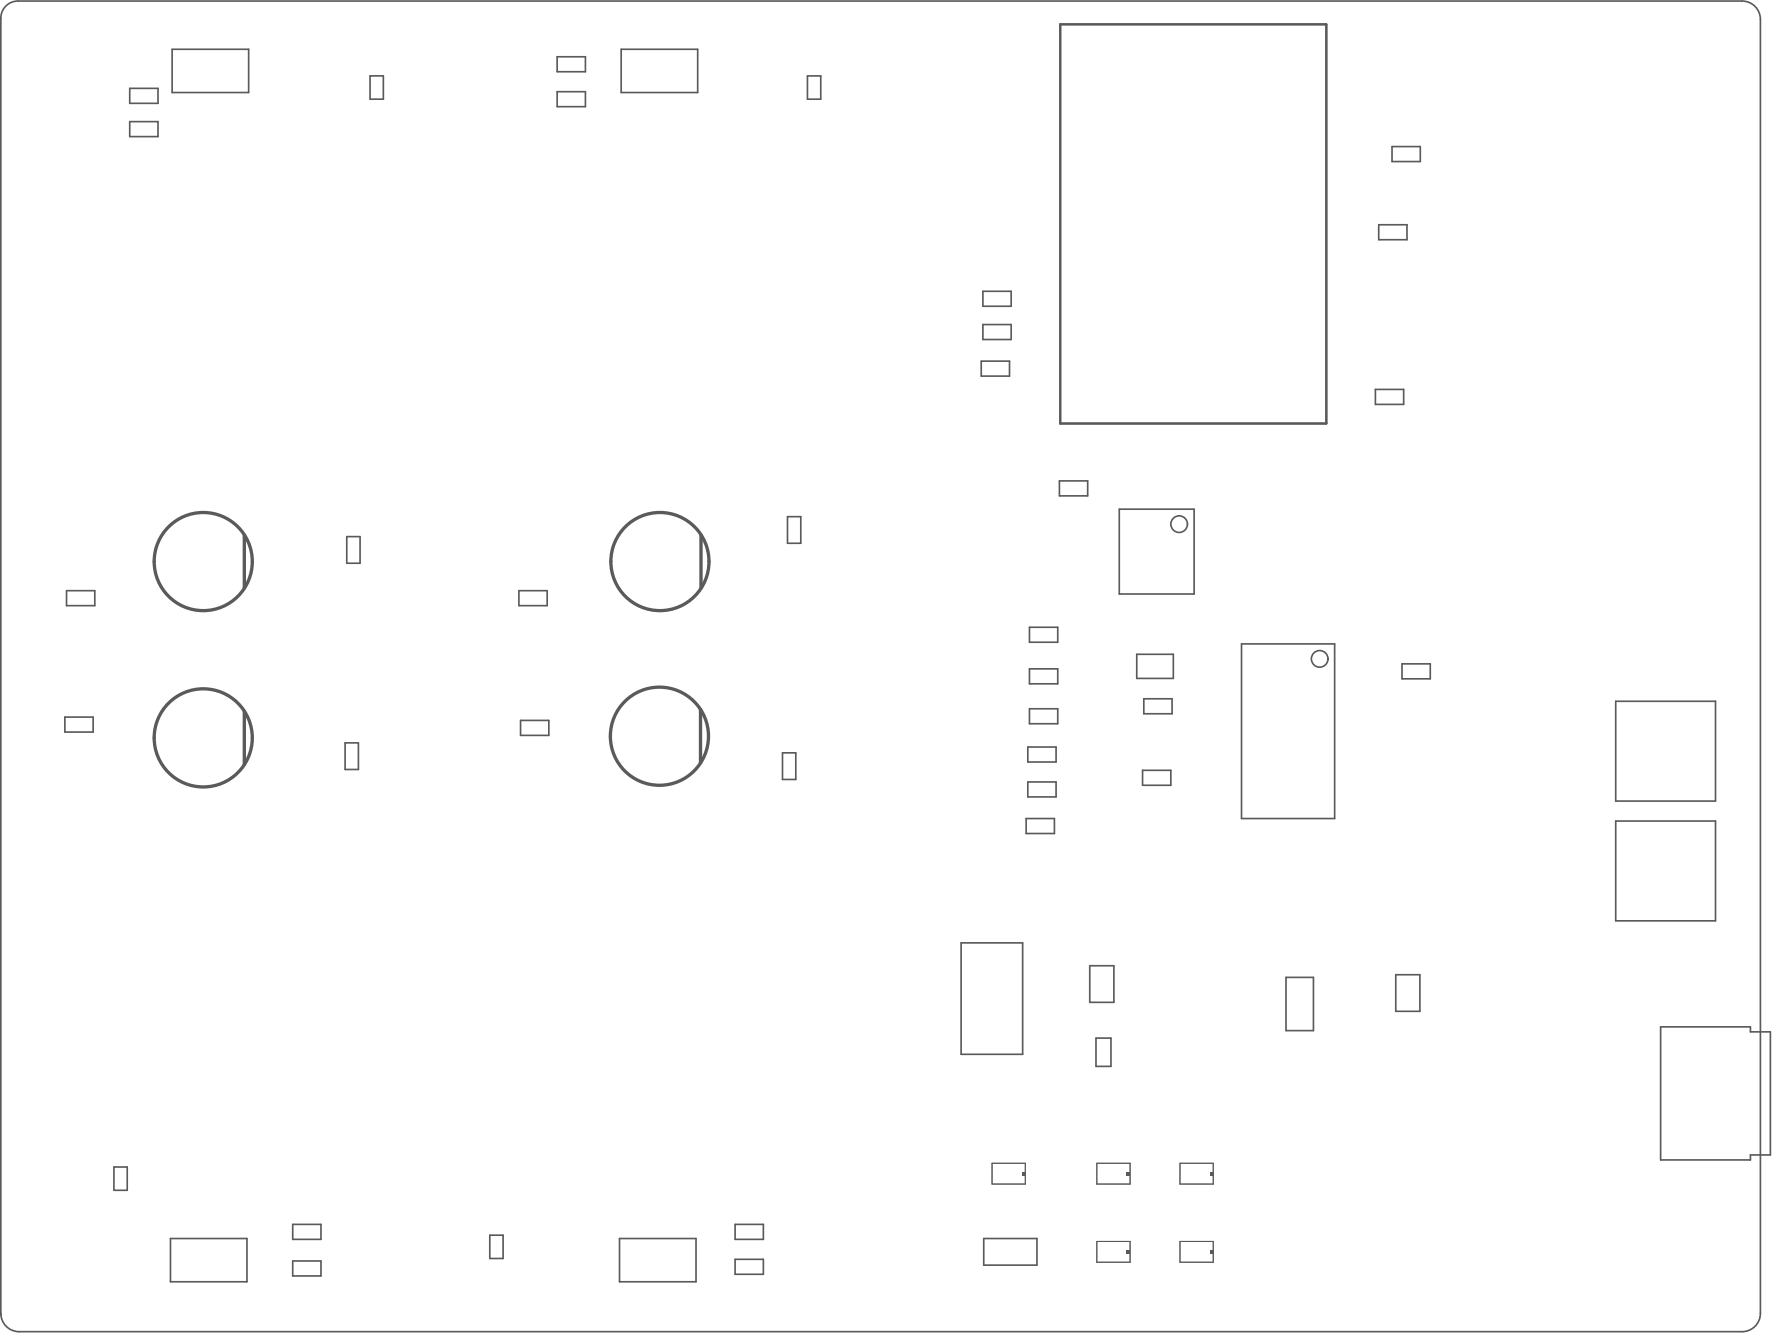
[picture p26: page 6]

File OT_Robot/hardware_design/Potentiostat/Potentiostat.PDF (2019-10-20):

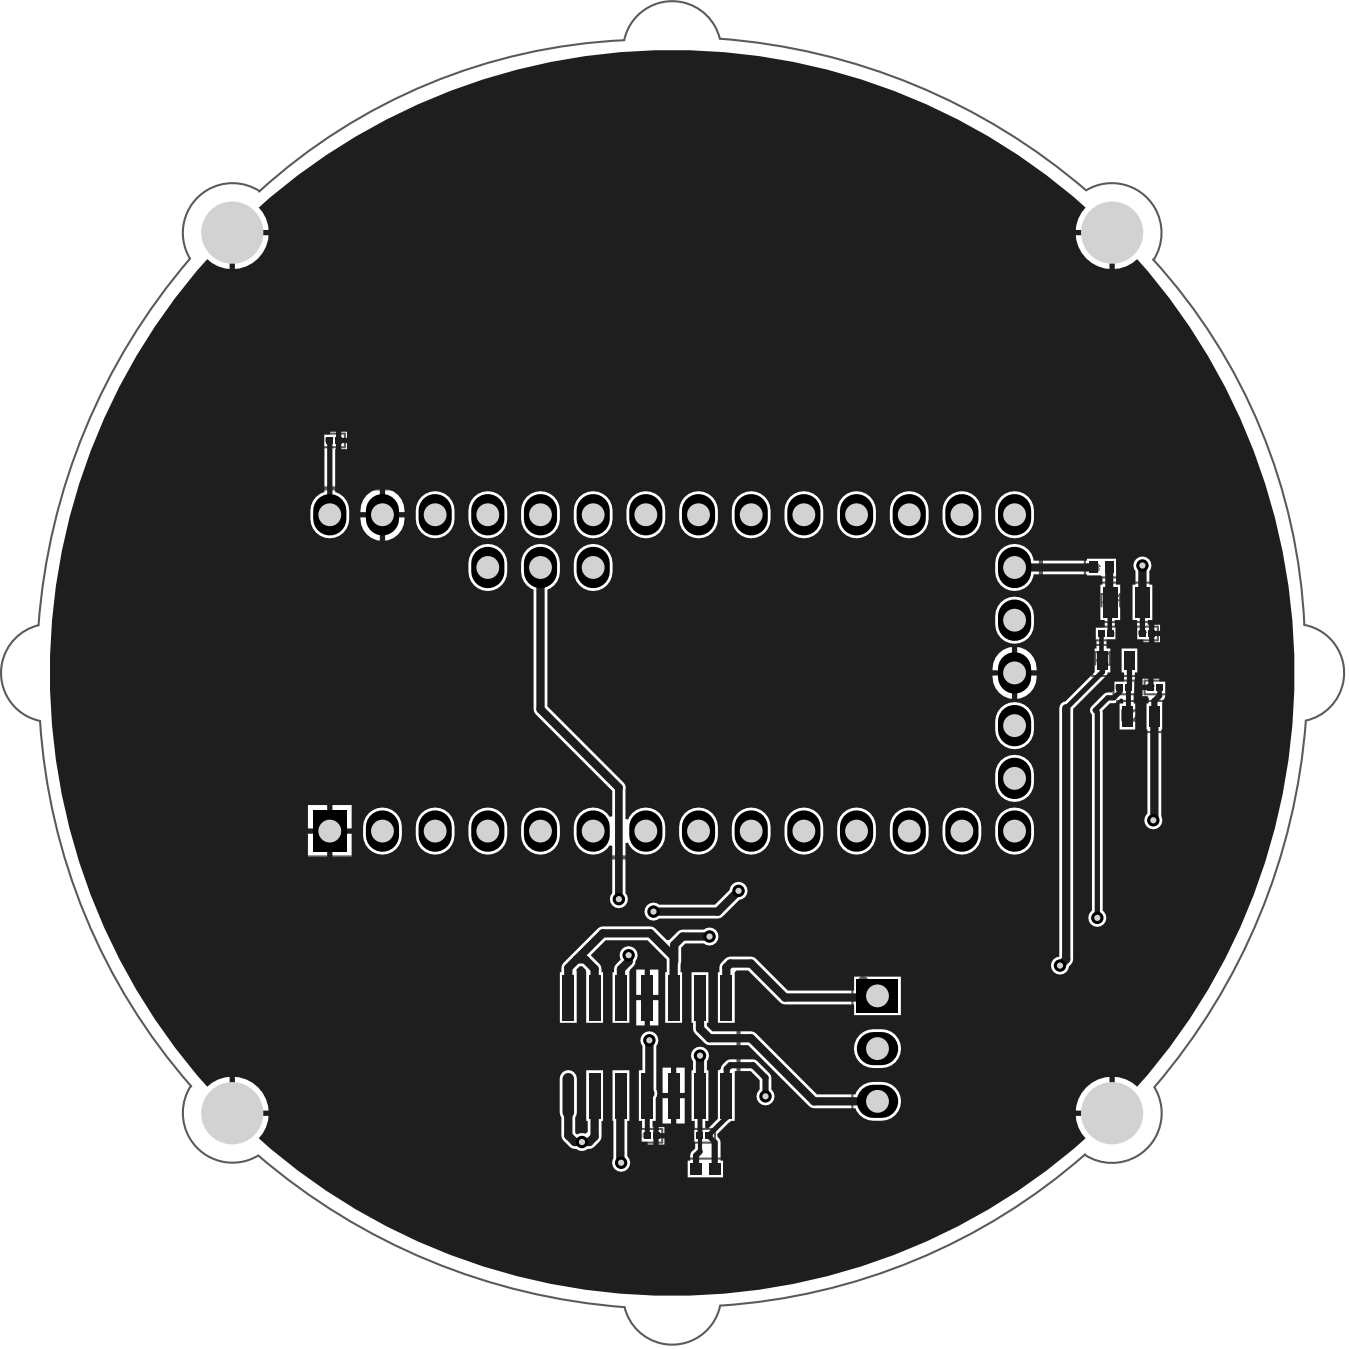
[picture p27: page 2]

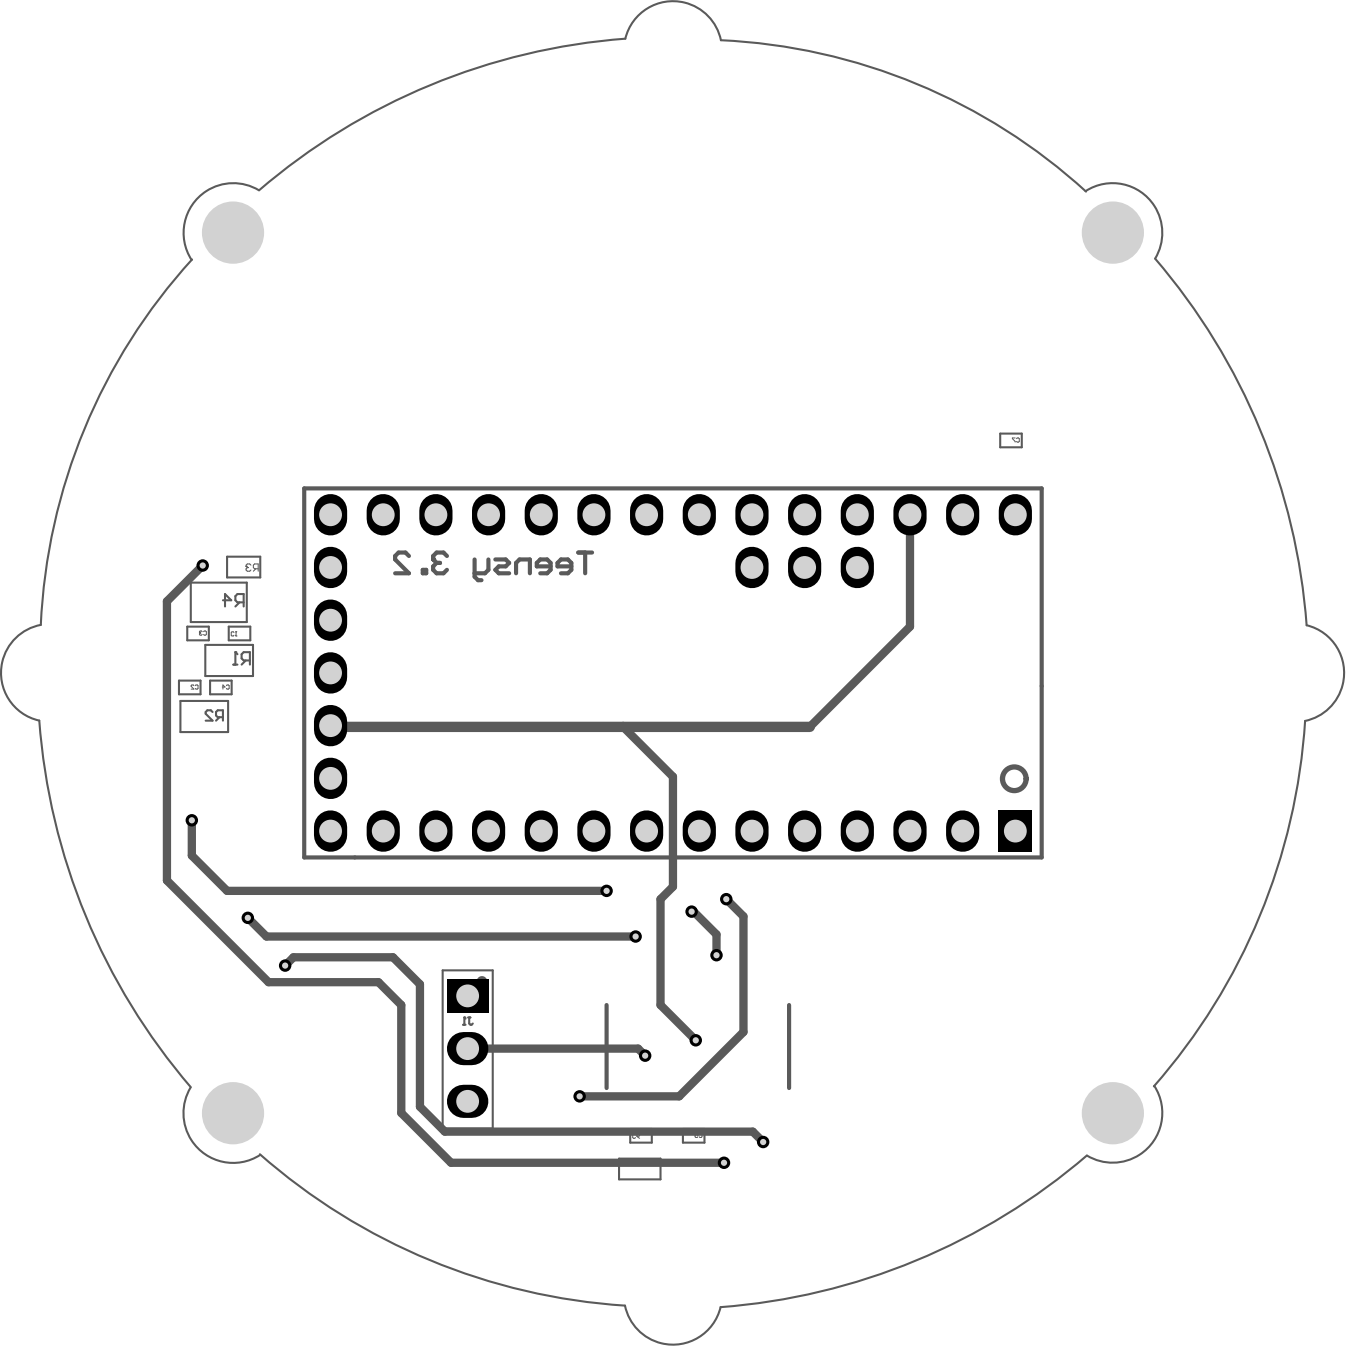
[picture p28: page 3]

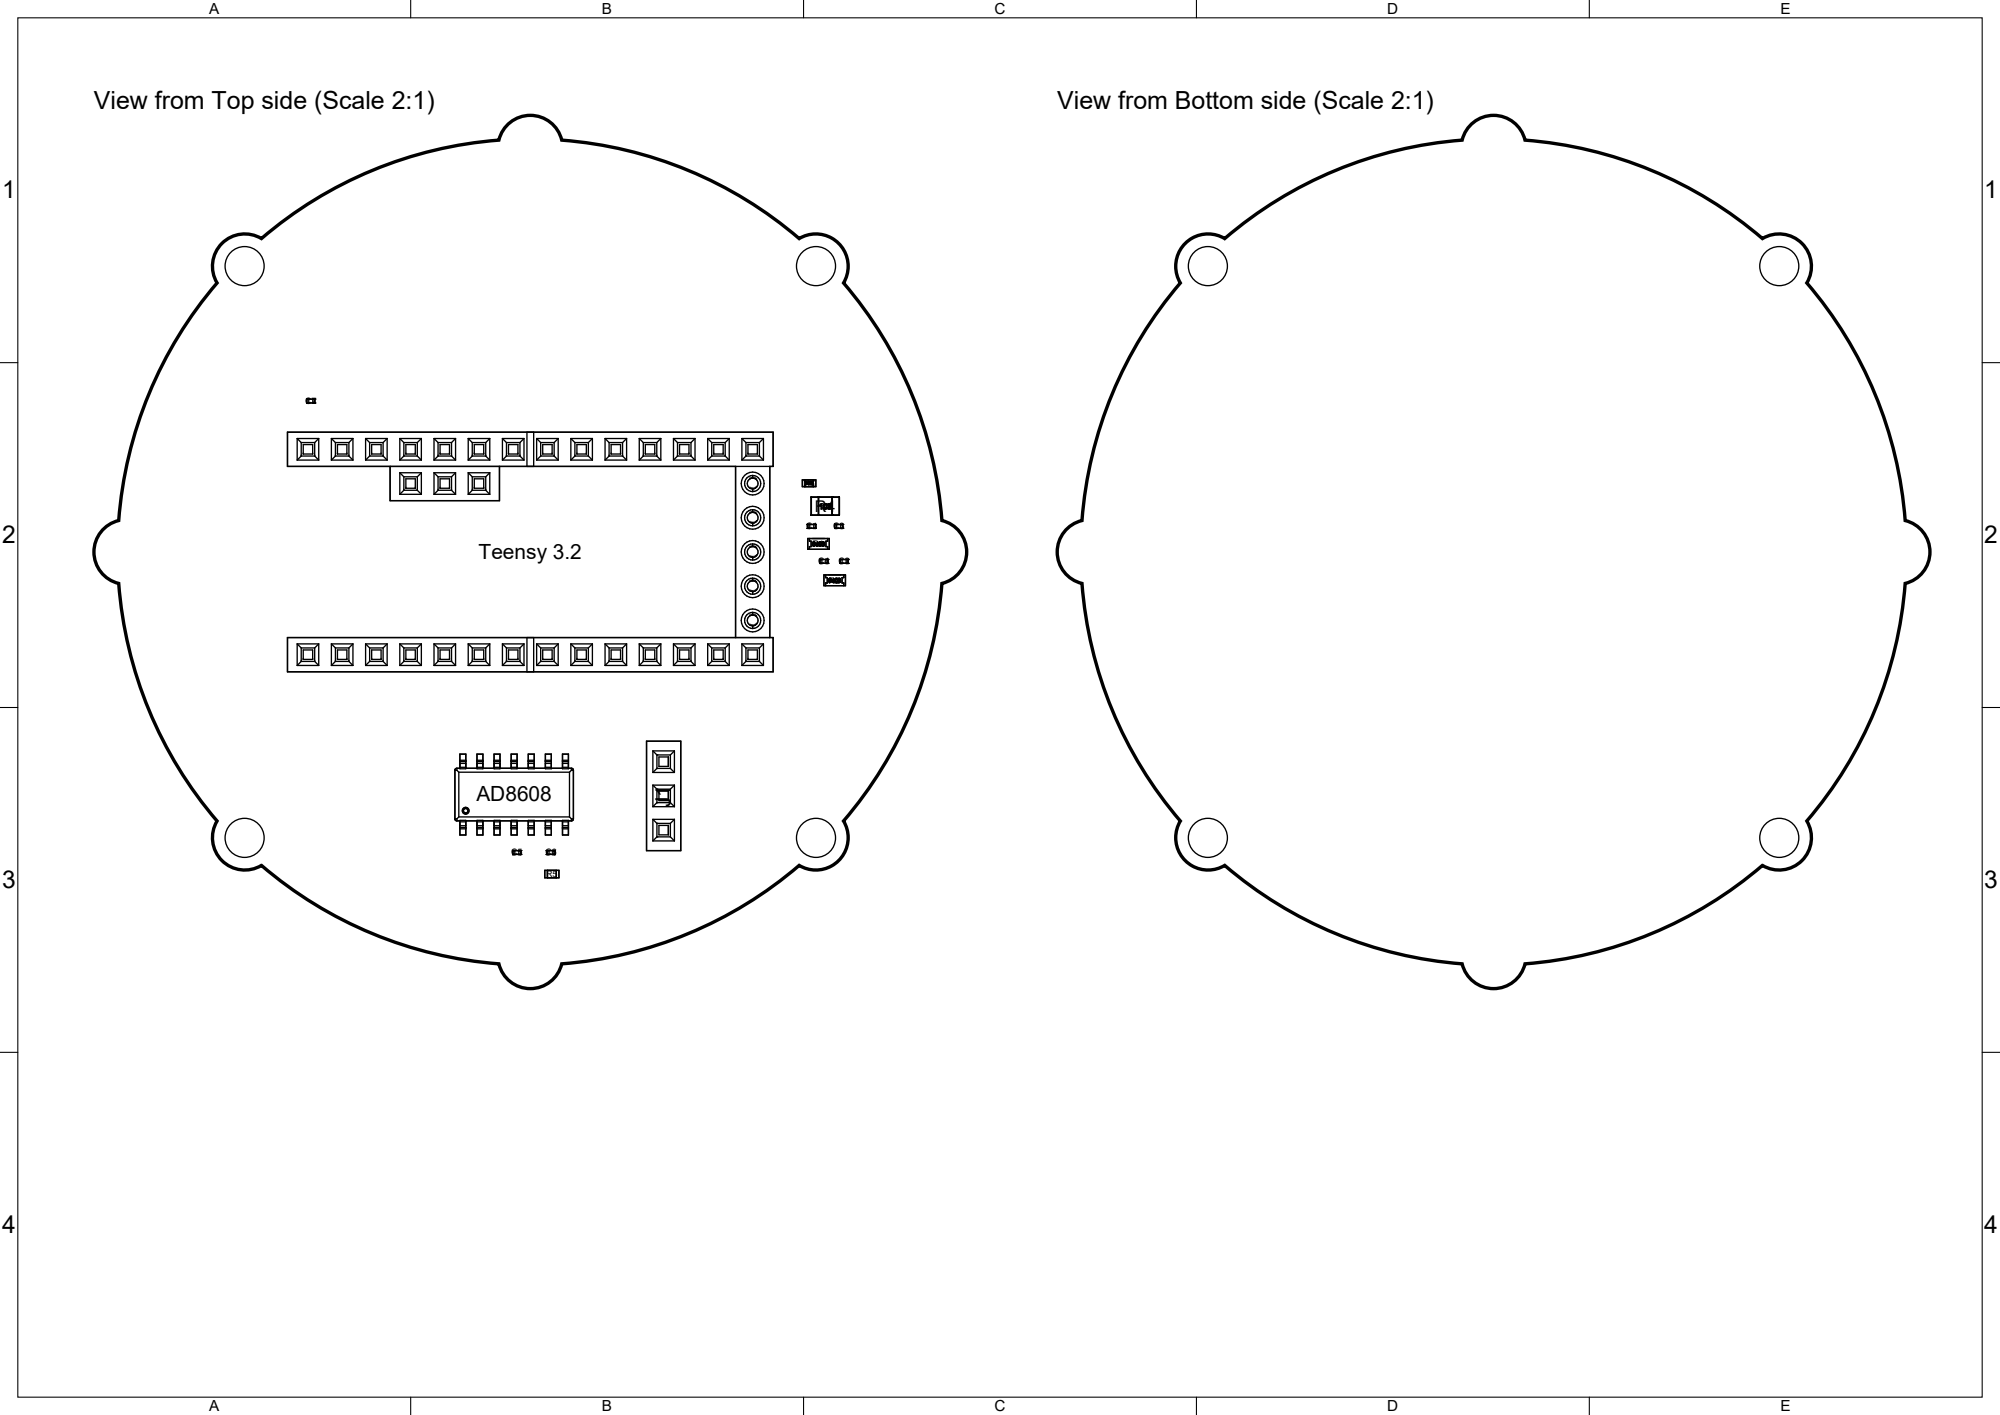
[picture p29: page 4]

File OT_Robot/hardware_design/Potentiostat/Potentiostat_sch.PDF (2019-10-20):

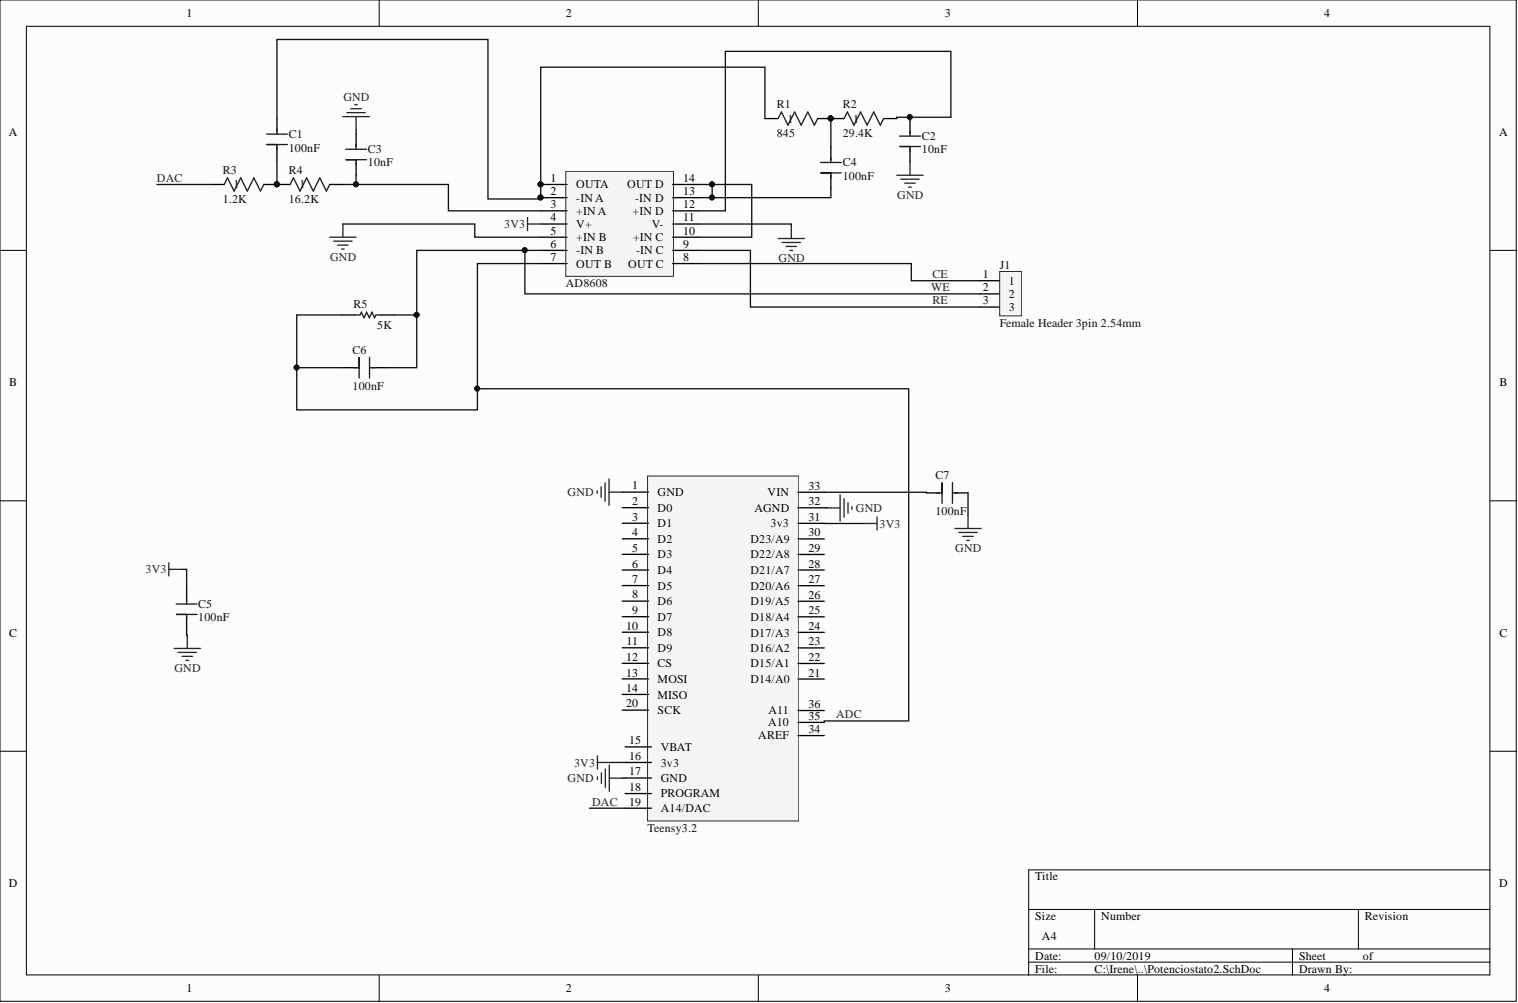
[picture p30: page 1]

OUT B 7 | GND

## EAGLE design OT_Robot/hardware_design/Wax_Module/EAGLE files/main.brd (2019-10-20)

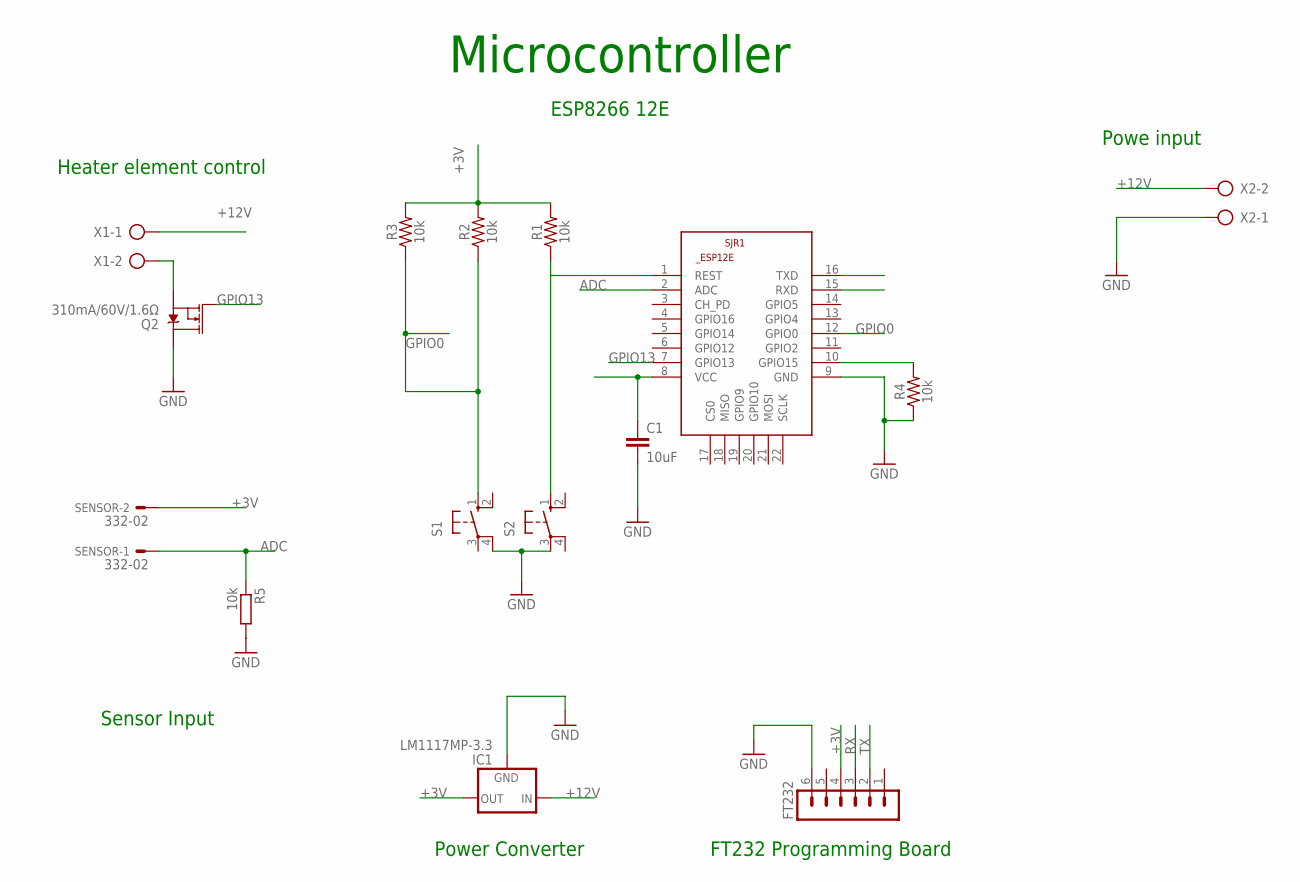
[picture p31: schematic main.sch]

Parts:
C1: 10uF; C1206
FT232: MA06-1
IC1: LM1117MP-3.3; SOT223
Q2: 310mA/60V/1.6Ω; SOT323
R1, R2, R3, R4: 10k; 0603
R5: 10k; R1206
S1, S2: 10-XX; B3F-10XX
SENSOR: 332-02
SJR1: ESP8266-12EESP12E; ESP8266-ESP12E
X1, X2: AK500/2

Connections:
+3V: C1.1, FT232.4, IC1.2 (OUT), IC1.4 (OUT), R1.2, R2.2, R3.2, SENSOR.2, SJR1.8 (VCC)
+12V: IC1.3 (IN), X1.1, X2.2
ADC: R5.1, SENSOR.1, SJR1.2 (ADC)
GND: C1.2, FT232.6, IC1.1 (GND), Q2.3 (D), R4.1, R5.2, S1.4 (P1), S2.3, SJR1.9 (GND), X2.1
GPIO0: R2.1, R3.1, S1.1 (S), SJR1.12 (GPIO0)
GPIO13: Q2.1 (G), SJR1.7 (GPIO13)
unnamed: Q2.2 (S), X1.2
unnamed: R1.1, S2.1 (S), SJR1.1 (REST)
unnamed: R4.2, SJR1.10 (GPIO15)
RX: FT232.3, SJR1.15 (RXD)
TX: FT232.2, SJR1.16 (TXD)

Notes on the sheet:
Microcontroller
ESP8266 12E
FT232 Programming Board
Power Converter
Sensor Input
Heater element control
Powe input

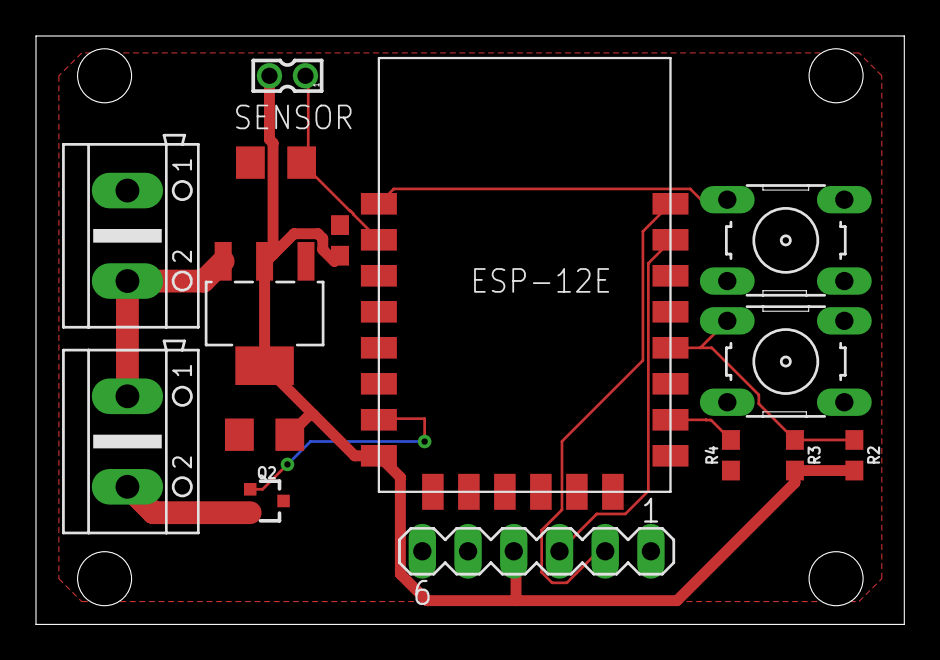
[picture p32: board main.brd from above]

Board: 2 copper layers, 48.2 x 32.7 mm, 15 parts (0 on the bottom side), 11 nets.

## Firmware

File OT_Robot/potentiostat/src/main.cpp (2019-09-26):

#include "WProgram.h"
#include "potentiostat.h"

using namespace ps;

SystemState systemState;

/*
	int16_t adc_read(uint8_t mux) {
	  uint8_t low;

	  ADCSRA = (1<<ADEN) | ADC_PRESCALER;             // enable ADC
	  ADCSRB = (1<<ADHSM) | (mux & 0x20);             // high speed mode
	  ADMUX = aref | (mux & 0x1F);                    // configure mux input
	  ADCSRA = (1<<ADEN) | ADC_PRESCALER | (1<<ADSC); // start the conversion
 	  while (ADCSRA & (1<<ADSC)) ;                    // wait for result
	    low = ADCL;                                     // must read LSB first
	  return (ADCH << 8) | low;                       // must read MSB only once!
	}
*/

void timerCallback() {
    systemState.updateTestOnTimer();
}
/*
void serialEvent() {
    systemState.updateMessageData();
}*/

extern "C" int main(void)
{
#ifdef USING_MAKEFILE

	// To use Teensy 3.0 without Arduino, simply put your code here.
	// For example:

    Serial.begin(UsbSerialBaudrate);
    systemState.initialize();
    systemState.setTestTimerCallback(timerCallback);	
    //pinMode(A14, OUTPUT);
    //analogWriteResolution(12);
    //pinMode(A10, INPUT);
    //analogReadResolution(12);
    //analogWrite(A14, 2048);

    while(1) {
        systemState.processMessages();
        systemState.serviceDataBuffer();
        systemState.updateMessageData();
	//Serial.println(analogRead(A10));
        delay(10);
    }

/*
  	analogWriteResolution(12);
	analogReadResolution(10);
    analogReference(DEFAULT);

	Serial.begin(9600);

	pinMode(13, OUTPUT);
	pinMode(A10, INPUT);
    pinMode(A14, OUTPUT);
  	analogWrite(A14, 2000);


	while(1) {
	  digitalWrite(13,HIGH);
	  int rval = analogRead(A10);
	  Serial.println(rval);
	  delay(1000);
	  digitalWrite(13,LOW);
      delay(1000);
  	  analogWrite(A14, 1000);
	}
*/
#else
	// Arduino's main() function just calls setup() and loop()....
	setup();
	while (1) {
		loop();
		yield();
	}
#endif
}

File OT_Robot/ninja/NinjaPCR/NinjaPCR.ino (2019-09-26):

#include <LEAmDNS.h>
#include <LEAmDNS_lwIPdefs.h>
#include <ESP8266mDNS.h>
#include <LEAmDNS_Priv.h>
#include <ESP8266mDNS_Legacy.h>

/*
 *  openpcr.pde - OpenPCR control software.tt
 *  Copyright (C) 2010-2012 Josh Perfetto. All Rights Reserved.
 *
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
 *  You should have received a copy of the GNU General Public License along with
 *  the OpenPCR control software.  If not, see <http://www.gnu.org/licenses/>.
 */

#include <LiquidCrystal.h>
#include <EEPROM.h>

#include "pcr_includes.h"
#include "adc.h"
#include "thermocycler.h"
#include "thermistors.h"
#include <ESP8266WiFi.h>
#include <ESP8266WebServer.h>
#include <ESP8266WiFiMulti.h>
#include <ESP8266HTTPClient.h>
#include "serialcontrol_chrome.h"
#include "wifi_communicator.h"

Servo LidServo;


#ifdef DEBUG
String debug = "NINJAPCR_DEBUG";
#endif
#ifdef DEBUG_NETWORK
String debugNetwork = "NINJAPCR_DEBUG_NETWORK";
#endif
#ifdef DEBUG_ADC
String debugADC = "NINJAPCR_DEBUG_ADC";
#endif
#ifdef DEBUG_ESP_CORE
String debugEspCore = "NINJAPCR_DEBUG_ESP_CORE";
#endif
#ifdef DEBUG_ESP_SSL
String debugEspSSL = "NINJAPCR_DEBUG_ESP_SSL";
#endif
#ifdef DEBUG_ESP_WIFI
String debugEspWiFi = "NINJAPCR_DEBUG_ESP_WIFI";
#endif
#ifdef DEBUG_ESP_HTTP_CLIENT
String debugEspHTTPClient = "NINJAPCR_DEBUG_ESP_HTTP_CLIENT";
#endif
#ifdef DEBUG_ESP_HTTP_UPDATE
String debugEspHTTPUpdate = "NINJAPCR_DEBUG_ESP_HTTP_UPDATE";
#endif
#ifdef DEBUG_ESP_HTTP_SERVER
String debugEspHTTPServer = "NINJAPCR_DEBUG_ESP_HTTP_SERVER";
#endif
#ifdef DEBUG_ESP_UPDATER
String debugEspUpdater = "NINJAPCR_DEBUG_ESP_UPDATER";
#endif
#ifdef DEBUG_ESP_OTA
String debugEspOTA = "NINJAPCR_DEBUG_ESP_OTA";
#endif

String versionDescription = FIRMWARE_VERSION_DESCRIPTION; // NEVER REMOVE THIS LINE!

Thermocycler* gpThermocycler = NULL;
WifiCommunicator *wifi = NULL;

boolean isInitialStart() {
    for (int i = 0; i < 50; i++) {
        if (EEPROM.read(i) != 0xFF)
            return false;
    }
    return true;
}

const SPIDTuning LID_PID_GAIN_SCHEDULE2[] =
    {
    //maxTemp, kP, kI, kD
                { 70, 40, 0.15, 60 },
                { 200, 80, 1.1, 10 } };

bool isApMode = false;

void setup() {


#ifdef USE_AUTOMATED_LID
    //********** CHANGE SERIAL PIN FUNCTION  TO GPIO **********
    //GPIO 3 (RX) swap the pin to a GPIO.
    pinMode(3, FUNCTION_3); 
    //**************************************************

    LidServo.attach(1);
    LidServo.write(180);
#else
    Serial.begin(BAUD_RATE);
#endif
    
    pinMode(PIN_WIFI_MODE, INPUT);
    delay(100);
    isApMode = (digitalRead(PIN_WIFI_MODE)==VALUE_WIFI_MODE_AP);
    delay(250);
    PCR_DEBUG("NinjaPCR Custom ver. ");
    PCR_DEBUG_LINE(OPENPCR_FIRMWARE_VERSION_STRING);
    initHardware();
    EEPROM.begin(1024);

    PCR_DEBUG("PIN_WIFI_MODE=");
    PCR_DEBUG_LINE(isApMode);
    if (isApMode) {
        PCR_DEBUG_LINE("AP mode");
        startWiFiAPMode();

        // Init AP mode
        setup_normal();
        wifi = new WifiCommunicator(wifi_receive, wifi_send);
        gpThermocycler->SetCommunicator(wifi);
    }
    else {
        PCR_DEBUG_LINE("HTTP Server mode");
  #ifdef USE_FAN
    digitalWrite(PIN_FAN, PIN_FAN_VALUE_ON);
  #endif
        startWiFiHTTPServerMode();
        setup_normal();
        wifi = new WifiCommunicator(wifi_receive, wifi_send);
        gpThermocycler->SetCommunicator(wifi);
    }
}

void setup_normal() {

#ifdef USE_STATUS_PINS
    pinMode(PIN_STATUS_A,OUTPUT);
    pinMode(PIN_STATUS_B,OUTPUT);
    digitalWrite(PIN_STATUS_A,LOW);
    digitalWrite(PIN_STATUS_B,LOW);
#endif /* USE_STATUS_PINS */

    //init factory settings
    /*
    if (isInitialStart()) {
        EEPROM.write(0, 100); // set contrast to 100
    }
    */
    //restart detection

#ifdef USE_WIFI
    //TODO EEPROM
    boolean restarted = false;
#else
    boolean restarted = !(MCUSR & 1);
    MCUSR &= 0xFE;
#endif /* USE_WIFI */

#ifdef USE_STATUS_PINS
    digitalWrite(PIN_STATUS_A, HIGH);
#endif /* USE_STATUS_PINS */
    gpThermocycler = new Thermocycler(restarted);
}

bool isSerialConnected = false;
bool initDone = false;
short INTERVAL_MSEC = 1000;

int sec = 0;
bool finishSent = false;
void loop() {
    unsigned long startMillis;
    unsigned long elapsed;

    /*
    if (isApMode) {
        delay(100);
        loopWiFiAP();
        return;
    }
    */

    startMillis = millis();
    /*
     * Pause heating & cooling units while processing HTTP requests
     * to avoid overheating
     */
    gpThermocycler->PauseHeatUnits();
    if (isWiFiConnected()) {
        loopWiFiHTTPServer();
    }

    elapsed = millis() - startMillis;
    if (elapsed<0 || elapsed > INTERVAL_MSEC) {
        elapsed = 0;
    }
    double powerOutputRatio = (double)INTERVAL_MSEC/(double)max(INTERVAL_MSEC/2, INTERVAL_MSEC-elapsed);
    PCR_DEBUG("powerOutputRatio=");
    PCR_DEBUG_LINE(powerOutputRatio);
    gpThermocycler->SetPowerOutputRatio(powerOutputRatio);
    gpThermocycler->Loop();

    if (gpThermocycler->GetProgramState() == Thermocycler::ProgramState::EComplete) {
        PCR_DEBUG_LINE("COMPLETE");
        if (!finishSent) {
            // TODO call IFTTT API if needed
            finishSent = true;
        }
    }
    delay(INTERVAL_MSEC-elapsed);
}

bool startLamp = false;
void checkSerialConnection() {
    PCR_DEBUG("pcr1.2"); //TODO
    //Serial.print("\n");
#ifdef USE_STATUS_PINS
    digitalWrite(PIN_STATUS_A, (startLamp)?HIGH:LOW);
#endif /* USE_STATUS_PINS */
    startLamp = !startLamp;
    unsigned long timeStart = millis();
    while (millis() < timeStart + INTERVAL_MSEC) {
        while (Serial.available()) {
            char ch = Serial.read();
            if (ch == 'a' && !isSerialConnected) {
#ifdef USE_STATUS_PINS
                digitalWrite(PIN_STATUS_A, LOW);
#endif /* USE_STATUS_PINS */
                isSerialConnected = true;
            }
        }
    }
}

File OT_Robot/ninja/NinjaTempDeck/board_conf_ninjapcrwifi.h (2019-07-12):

#ifndef ___BOARD_CONF_NINJAPCR___
#define ___BOARD_CONF_NINJAPCR___

#define BAUD_RATE 9600
/* Board Config */
#define USE_ESP8266

/* ADC (NAU7802 or MCP3554) */
#define USE_ADC_NAU7802
//#define USE_ADC_MCP3554
#define TEHRMISTORS_NINJAPCR

// Thermistor value is measured by 2 ranges, switched by analog switch
#define THERMISTOR_2_RANGES
#define PIN_THERMISTOR_RANGE_SWITCH 16 /* Analog switch */

#define USE_WIFI /* Use WiFi functionalities */
#define PIN_WIFI_MODE 16 /* Digitai input pin to switch AP (pairing) mode and Normal mode  */
#define VALUE_WIFI_MODE_AP HIGH /* Start with AP (pairing) mode if value of PIN_WIFI_MODE agrees with this.  */
// #define USE_LCD /* Use display */
// #define USE_STATUS_PINS /* Use status LEDs */
// #define DEBUG_DISPLAY

/* Use LCD */

/* LCD Pins (Dummy) */
#define PIN_LCD_RS 6
#define PIN_LCD_ENABLE 7
#define PIN_LCD_D4 8
//#define PIN_LCD_D5 A5
#define PIN_LCD_D5 5 // TMP
#define PIN_LCD_D6 16
#define PIN_LCD_D7 17
#define PIN_LCD_CONTRAST 5

/* Lid */
#define PIN_LID_THERMISTOR_AIN 1 // TODO Use TOUT
#define PIN_LID_PWM 15 // PWM is available
// #define PIN_LID_PWM_ACTIVE_LOW
#define USE_ESP8266

/* Well */
#ifdef  USE_ADC_NAU7802
#define PIN_WELL_INA 12
#endif
#ifdef USE_ADC_MCP3554
#define PIN_WELL_INA 12
#endif
#define PIN_WELL_INB 13
#define PIN_WELL_PWM 4
#define PIN_WELL_PWM_ACTIVE_LOW
#define PIN_WELL_HIGH_TEMP 16

/* Fan */
#define USE_FAN
#define PIN_FAN 0
#define PIN_FAN_VALUE_ON HIGH
#define PIN_FAN_VALUE_OFF LOW
/* Suppress frequent switching of relay */
#define SUPPRESS_PELTIER_SWITCHING
/*
 * Define on/off logic values according to
 * polarity of transistors for the relay
 */
#define PIN_WELL_VALUE_ON LOW
#define PIN_WELL_VALUE_OFF HIGH

/* SPI */
#define PIN_WELL_MCP3554_DATAOUT 13//MOSI (Not used)
#define PIN_WELL_MCP3554_DATAIN  12//MISO
#define PIN_WELL_MCP3554_SPICLOCK  14//sck
#define PIN_WELL_MCP3554_SLAVESELECT 5//ss


/* SPI */
#ifdef USE_ADC_MCP3554
#define PIN_WELL_MCP3554_DATAOUT 13//MOSI (Not used)
#define PIN_WELL_MCP3554_DATAIN  12//MISO
#define PIN_WELL_MCP3554_SPICLOCK  14//sck
#define PIN_WELL_MCP3554_SLAVESELECT 5//ss
#endif /* USE_ADC_MCP3554 */

#ifdef USE_ADC_NAU7802
#define PIN_WELL_NAU7802_SCL 14
#define PIN_WELL_NAU7802_SDA 2
#define PIN_WELL_NAU7802_RDY 5
#endif /* USE_ADC_NAU7802 */

#define MIN_PELTIER_PWM -1023
#define MAX_PELTIER_PWM 1023

#define MAX_LID_PWM 1023
#define MIN_LID_PWM 0


#endif /* ___BOARD_CONF_NINJAPCR___ */

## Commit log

2019-07-26 Pcr graph, ninja driver, calibration test
2019-07-26 test.py well calibrated
2019-08-05 Changes for 300ul
2019-08-13 - Updated ninja driver: support for different labwares for PCR and TempDeck - separacion.py now uses the P300_Single pipette
2019-08-13 - Coating now uses the P300_Single pipette - Updated separacion - Updated tincion
2019-08-29 - Added teensy DAC control - Added mix_after in separation_cells - Elona corrections
2019-09-04 - Elona changes - Separation_cell changes - Uploaded rodeostat libraries to teensy-loader/libraries
2019-09-11 three threads
2019-09-11 Threads and letters
2019-09-12 Teensy potentiostat code
2019-09-13 Teensy changes
2019-09-13 Working teensy setup
2019-09-26 Teensy readme
2019-10-18 Hardware Design
    [Bearing_Part.stl, Bill of Materials-Fluorimetro_Project.xlsx, Bill of Materials-Potenciostato2_Project.xlsx, BodyBack.dwg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]
2019-10-19 New HW and design
    [Flurorimetro_PCB.GBL, Flurorimetro_PCB.GBO, Flurorimetro_PCB.GBP, Flurorimetro_PCB.GBS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]
2019-10-20 Solved HW issues
    [2 CORTOS & BACK.dwg, Base_Case.dwg, Bearing Piece.stl, Bearing_Part.stl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]
2019-11-24 lo voy a cambiar
    [Front.dwg]
2019-11-24 delete rside
    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
    [RSide.dwg]
2019-11-24 delete side
    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
    [Side.dwg]
2019-11-24 delete top
    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
    [Top.dwg]
2019-11-24 delete board
    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
    [board.dwg]
2019-11-24 delete inside
    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
    [inside.dwg]
2019-11-24 delete stamp1
    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
    [Membrane_Test_Stamp_1.stl]
2019-11-24 delete stamp2
    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
    [Membrane_Test_Stamp_2.stl]
2019-11-24 delete stamp3
    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
    [Membrane_Test_Stamp_3.stl]
2019-11-24 delete heater
    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
    [w1001_heater-lift.dwg]
2019-11-24 delete cover-top
    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
    [w1002_cover-top.dwg]
2019-11-24 delete cover-back
    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
    [w1003_cover-back-maker.dwg]
2019-11-24 delete cover-front
    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
    [w1004_cover-front-maker.dwg]
2019-11-24 delete cover-side
    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
    [w1005_cover-sides.dwg]
2019-11-24 delete cover-bottom
    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
    [w1006_cover-bottom.dwg]
2019-11-24 delete heatsink-hang
    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
    [w2001a_heatsink-hang-LGA115x.dwg]
2019-11-24 delete body-top
    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
    [w2002a_body-top-LGA115x-maker.dwg]
2019-11-24 delete peltier
    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
    [w2003_peltier-support.dwg]
2019-11-24 delete body-front
    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
    [w2003a_body-front-ver2.1-maker.dwg]
2019-11-24 delete body left
    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
    [w2004_body-left.dwg]
2019-11-24 delete body-back
    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
    [w2005_body-back.dwg]
2019-11-24 delete body bottom
    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
    [w2007_body-bottom.dwg]
2019-11-24 delete base
    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
    [Base_Case.dwg]
2019-11-24 delete back
    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
    [BodyBack.dwg]
2019-11-24 delete bottom
    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
    [BodyBottom.dwg]
2019-11-24 delete left
    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
    [BodyLeft.dwg]
2019-11-24 delete rigth
    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
    [BodyRight.dwg]
2019-11-24 delete heatsink
    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
    [Heatsink.dwg]
2019-11-24 delete pcbwood
    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
    [PCBWood.dwg]
2019-11-24 piezas sustituidas
    [All.dwg, Back.dxf, Board.dxf, Front.dxf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]

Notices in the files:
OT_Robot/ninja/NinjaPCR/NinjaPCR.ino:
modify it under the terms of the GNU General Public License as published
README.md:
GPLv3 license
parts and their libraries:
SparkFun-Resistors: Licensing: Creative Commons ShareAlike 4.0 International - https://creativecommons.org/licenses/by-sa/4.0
